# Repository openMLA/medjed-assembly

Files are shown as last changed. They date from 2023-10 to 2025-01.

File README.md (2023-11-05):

# Medjed Assembly

This repository contains the CAD files and assembly of the [MEDJED Maskless lithography system](https://github.com/openMLA/Medjed). CAD files are generated with FreeCAD.

Note that the [Wiki](https://github.com/openMLA/Medjed/wiki) and [Discussions](https://github.com/openMLA/Medjed/discussions) for the project are located in the main Medjed repository.

### Organisation

This repository should generally be obtained as a submodule of the main Medjed repository. That other repository will also have code and PCB designs for the project. 

The binary files are managed through [git-annex](https://git-annex.branchable.com/). When you first clone this repository these files will not have been downloaded, so you will see the history of the files, but not be able to open them.

To download these files, simply run (in git bash, or some terminal with git support)

``` shell
git-annex get .
```

Which should download all the files. If you only want a subset of the files, you can also run e.g. ` git annex get /optics/*.FCStd`. The files are stored on a [google cloud storage special remote](https://gist.github.com/NemoAndrea/86f93e55a579ad4e2c7e8fea4603c1c2).

### Freecad Configuration

The project uses two FreeCAD plugins, and it is recommended you install these before working with the files. You can easily install these with the built-in plugin manager of FreeCAD.

1. [Assembly 4 workbench 🏗](https://github.com/Zolko-123/FreeCAD_Assembly4)
2. [Optics workbench 🔍](https://github.com/chbergmann/OpticsWorkbench)
3. [KicadStepUp ⚡](https://github.com/easyw/kicadStepUpMod)

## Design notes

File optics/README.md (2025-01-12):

# Medjed Optics



### A quick note on motivations

The optical design is not designed to reach the absolute lowest cost possible, but rather prioritises the long-term availability of the components and ease of part sourcing. As such, many parts will be sourced from Thorlabs , and supplemented with 3D printed parts where possible. When components are chosen, they will still generally be on the lower-end of parts, as the Medjed is not a high resolution optical system (compared to what one may typically make with Thorlabs parts.)

For more detailed justifications for part choices and focal length, consult the [wiki page](../../Medjed.wiki/optics.md)



### A note on organisation

There are 3 different big assemblies in the origin. This is a bit confusing, but this was the only way to get around the "1 assembly per file" constraint of the `Assembly4` workbench. 

1. `assembly-optical` is the base assembly, which contains the base UV unit of the Photon Ultra.
2. `assembly-optical-stock` is the optical assembly, as used in the photon ultra (i.e. base assembly + lens)
3. `assembly-optical-medjed` is the main optics for the Medjed system.  **🔎 This is the main file to explore.**

## ☀ Ray Tracing with the Optics workbench

For the 60mm doublet I have used a fixed refractive index evaluated at 630nm. This is because the optics workbench does not support Cauchy coefficients, which are [the ones listed for the glass variants used in the lens](https://refractiveindex.info/?shelf=glass&book=HOYA-FD&page=E-FD10).

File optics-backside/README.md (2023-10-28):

### External models

The model for the Raspberry Pi Camera V2.1 was created by thingiverse user `soswow` and is available at https://www.thingiverse.com/thing:2376448/files.     The model was downloaded as an `.igs` file on 2023-06-11 and modified for purposes of the project.

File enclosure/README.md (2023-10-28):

## Medjed Enclosure

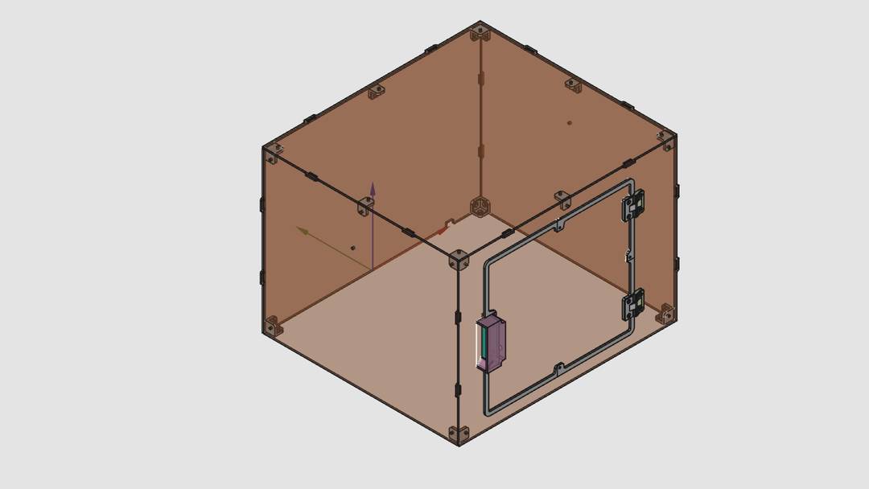
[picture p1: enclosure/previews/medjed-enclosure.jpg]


The FreeCAD file in this directory can be used to export `.dxf` files that define cut lines for acrylic panels.  In addition, there are printed parts that can be printed on a standard filament 3D printer. PLA is probably adequate, but if you plan on treating it particularly aggressively you may want to print the structural pieces out of PETG.

Use the **legacy** exporter for dxf, as the new one has some issue at time of writing (2023).

There are 5 panels total

* Front panel (this one is kept as a solid piece, to lower costs; some separation needed when you receive it)
* Back panel
* Side panel 1
* Side panel 2 (identical to panel 1)
* Top panel



The design features print-in-place hinges, which seem to print fine out of PLA, long term durability unknown. Print settings: Prusa Mini+. Polyterra PLA, 0.4mm nozzle, 0.2mm layer height.



###  Parts list

1. Acrylic panels (3mm thick; for thicker panels you need to adjust the designs a bit)
2. 3D printed parts (PLA seems to work OK, PETG preferred)
4. [Omron micro switch: D2F-01F-D](https://nl.rs-online.com/web/p/micro-switches/6867688)
5. M5 nut (with plastic collar would be preferred) [4X]
6. M4 bolts (10mm shaft length) and nuts (with plastic collar would be preferred) [35X]
7. M2 bolts and nuts for micro switch attachment [2X]

### Material choice

I suggest you have the enclosure cut out of orange acrylic. Ideally, choose an acrylic material of which you know the absorption at the relevant wavelengths (centered at 405nm, but consider 390-420). It would be good to have the enclosure made out of material with high absorption in this range (99.9%+). Since the focus of the objective (and hence the UV) is always far away from the user (provided they are not inside the enclosure) very high OD is not needed I suspect (please check safety considerations by yourself).

Something like 

* Plexiglas `ORANGE 2C04`
* Green Cast `orange`

*Note that neither of the above have published transmission spectra (that I could find), and may still transmit a significant amount of UV light.*

> **Note**
>
> There is a small test object in the main freecad file that you can order before ordering the main pieces. That tolerance piece can help you tune the tolerances of your cut acrylic supplier.

### A note on DXF export

The FreeCAD `.dxf` export produces files that may not be interpreted correctly by all manufacturers. A solution it to take legacy-dxf export from FreeCAD and open and re-export it via Fusion360. 

If you don't need to modify the panels yourself you can also use the provided [`.dxf` files](./dxf)

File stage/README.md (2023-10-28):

# XY stage

The XY stage has the following limits:

---

With Base 4-inch stage

X: 158mm (Z-axis prevents movement)

Y: 168mm 

---

With no stage (just the snapmaker carriage)

X: 168mm 

Y: 168mm 

## Sample chuck

The sample chuck PCB would ideally sit at such height that the UV sensor active area is exactly the sample height. For a typical Si sample: 0.5mm. Doing so, however, would mean the PCB and components stick out above the chuck's surface level. I think this is not ideal as it limits the sample size but also increases risk of collision.

The three ICs on the frontside have the following max heights:

* ICM42605: 0.97mm
* OPT3002: 0.65mm
* SHT45 (with PTFE filter): 0.79

Accounting for solder height and maybe poor seating I think recessing the PCB surface 1.5mm below the chuck should be adequate.

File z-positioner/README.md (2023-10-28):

## Fine Z-axis

The Medjed system needs to be able to focus the objective with a precision at least as good as the lateral resolution (5um target). The coarse Z-motors will not even get close to this. 

Thus, a separate fine focus mechanism is needed. 

**🏗 This this still in the prototype phase, please check out the GitHub discussions to see latest in development and experiments regarding this component.**

### Z positioner based on linear rail

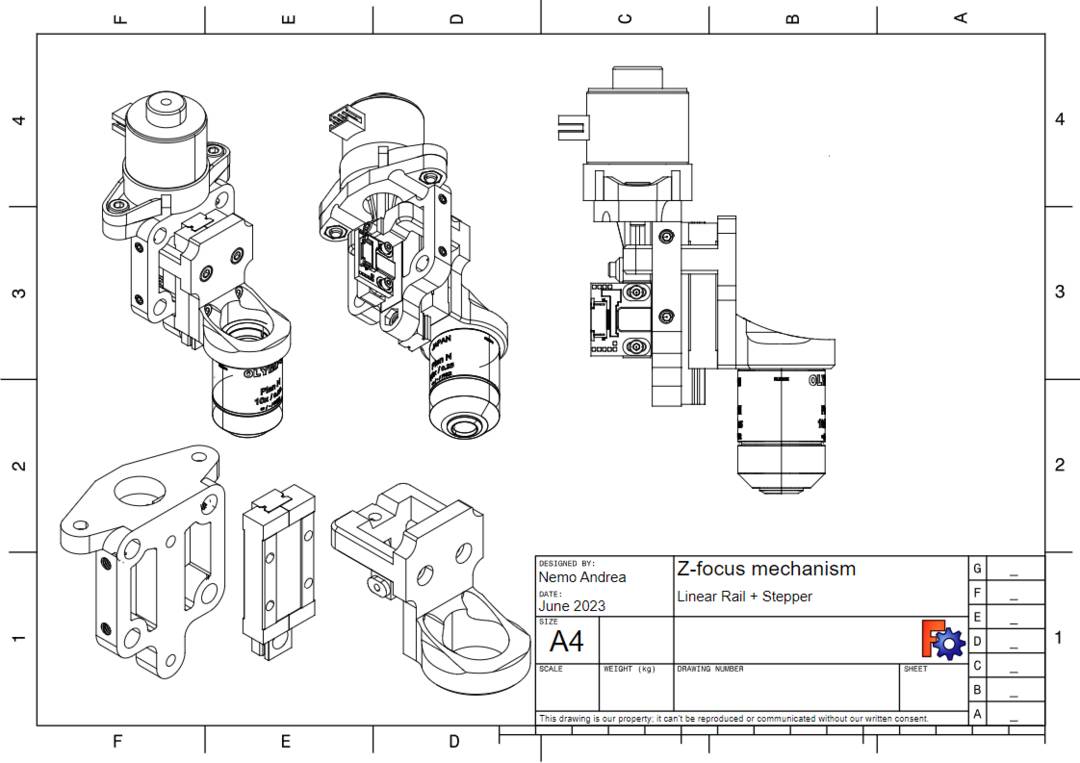
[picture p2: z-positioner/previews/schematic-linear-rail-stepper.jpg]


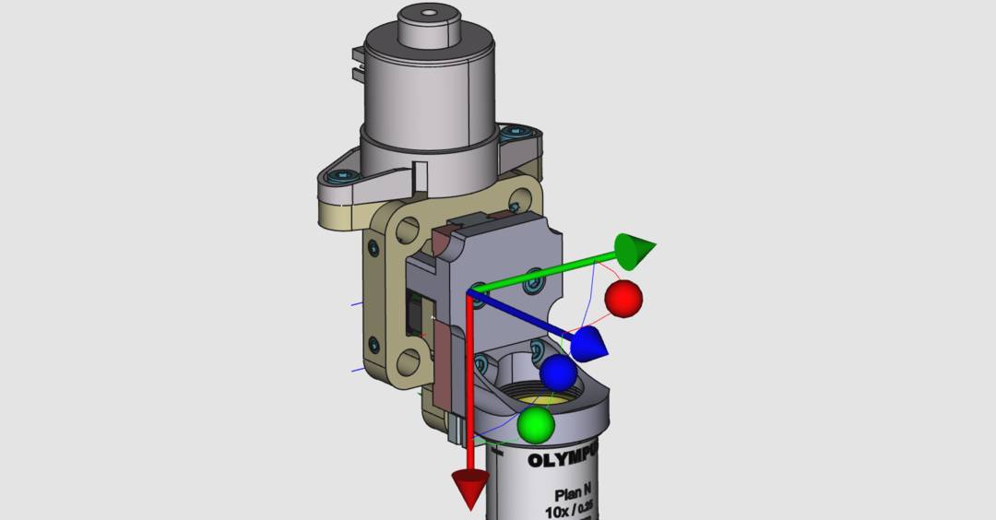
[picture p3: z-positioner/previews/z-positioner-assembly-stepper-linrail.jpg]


[Open in FreeCAD](z-positioner-assembly-stepper-linrail.FCStd)

Besides the linear rail, and encoder, you will need the following bits:

* 2x M4 (ISO 4762) bolts for stepper mount. 8 or 10 mm length.
* 2x M4 hex nuts (ISO 4032)
* 4x M3 4mm (ISO 4762) to mount objective bracket to rail
* 2x M3.5 8mm (ISO 4762) to mount rail to cage bracket
* 2x M3.5 hex nuts (ISO 4032)
* 4x M4 grub screw (ISO 4026) to secure the part against the cage rods
* 2x M2 10mm (ISO 4762) for encoder mounting
* 2x M2 hex nuts (ISO 4032)

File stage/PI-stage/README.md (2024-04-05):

# Physik Instrumente Stage

For development purposes, a PI M-525.2MO stage will be used. It uses small crossed roller bearings and stepper motors (M-229.25S; 10um backlash, 2um repeatability). The Steppers and encoders can be read out via python with the `pipython` python package.

A basic stage is built up around this system.

In the final product a custom replacement for the stage will be required, as it is neither fast enough, nor cheap enough to really serve as a good fit for the Medjed project.

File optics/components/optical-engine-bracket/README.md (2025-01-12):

# Optical Engine Bracket

This part connects the eViewTek optical engine to the rest of the build.

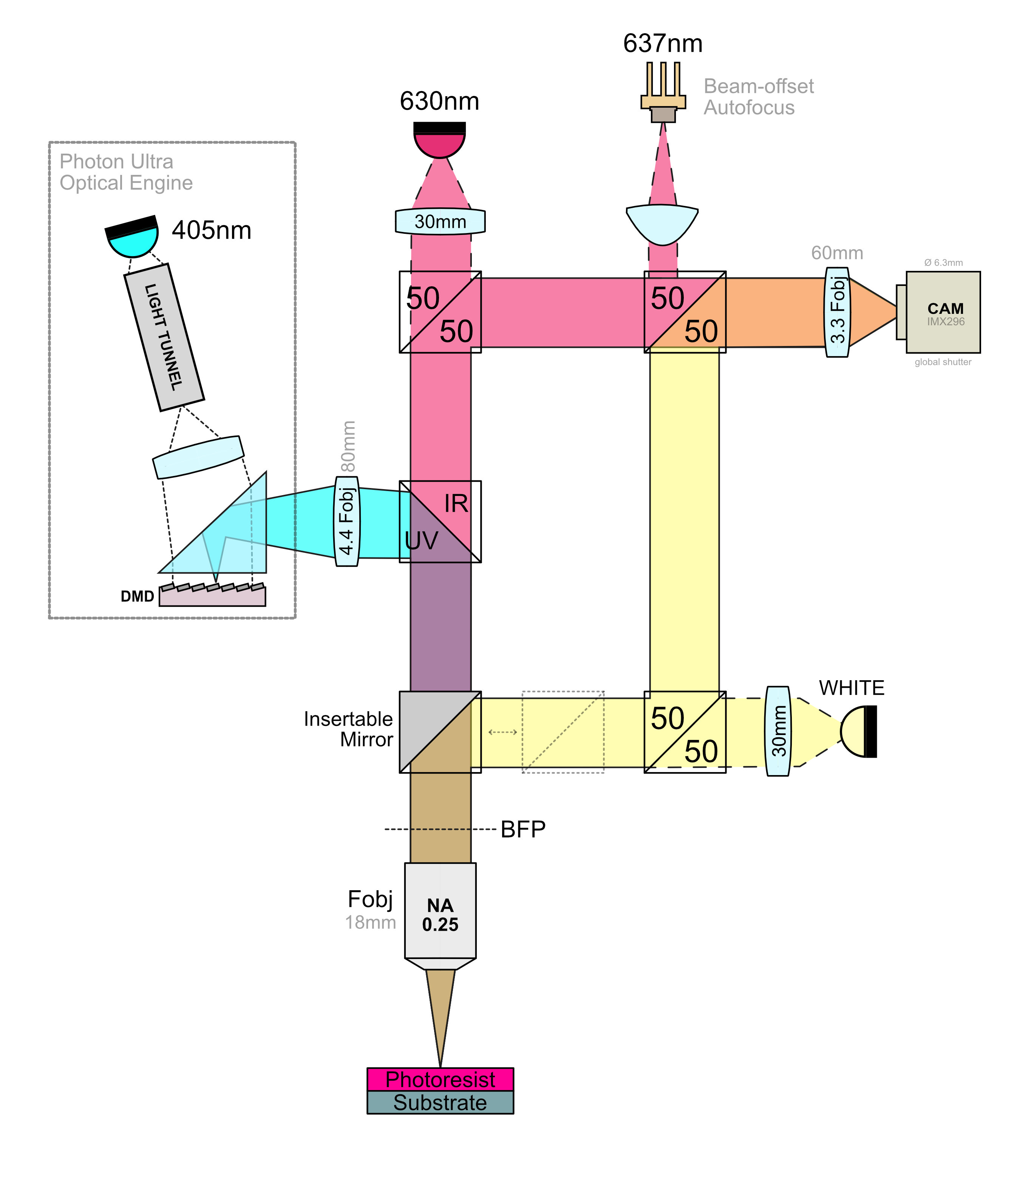
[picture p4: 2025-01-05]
media/optical_diagram.jpg

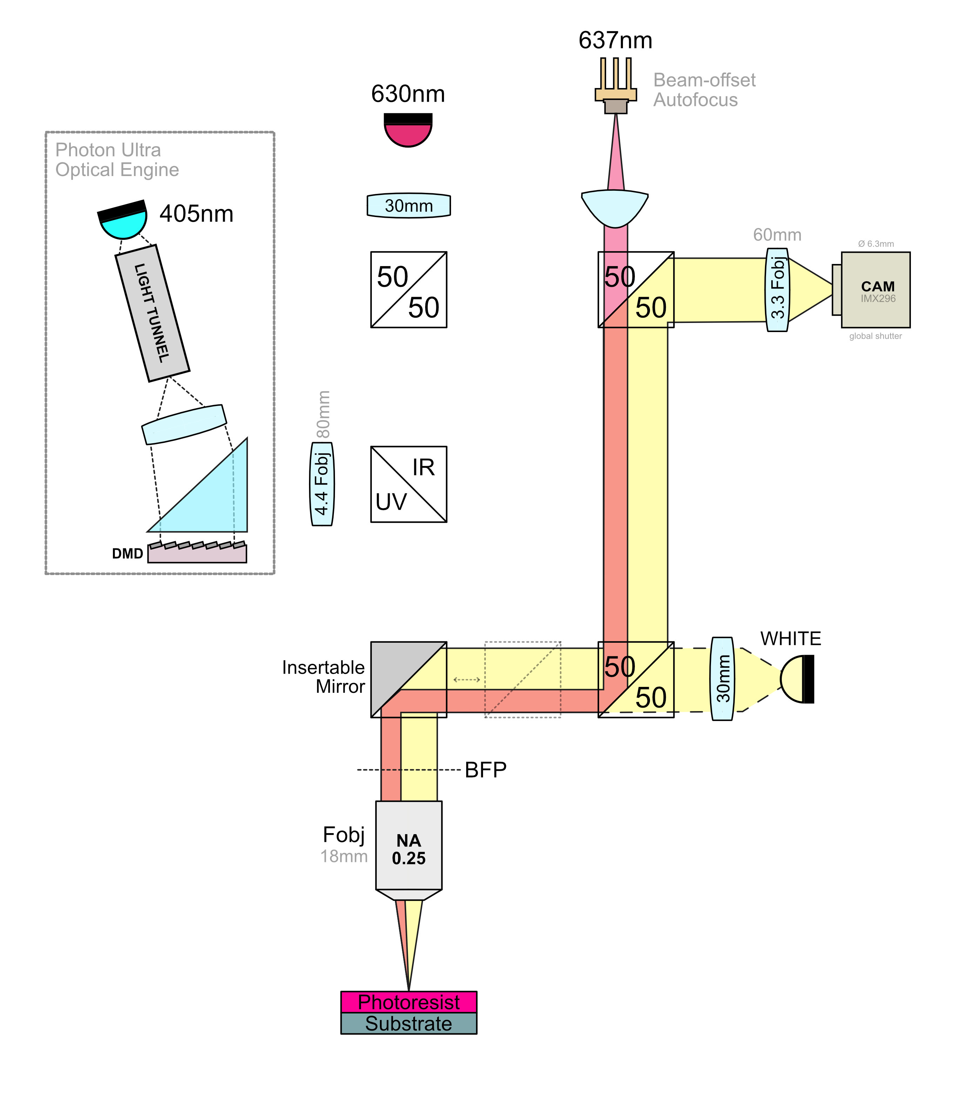
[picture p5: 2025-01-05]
media/optical_diagram-whitelight.jpg

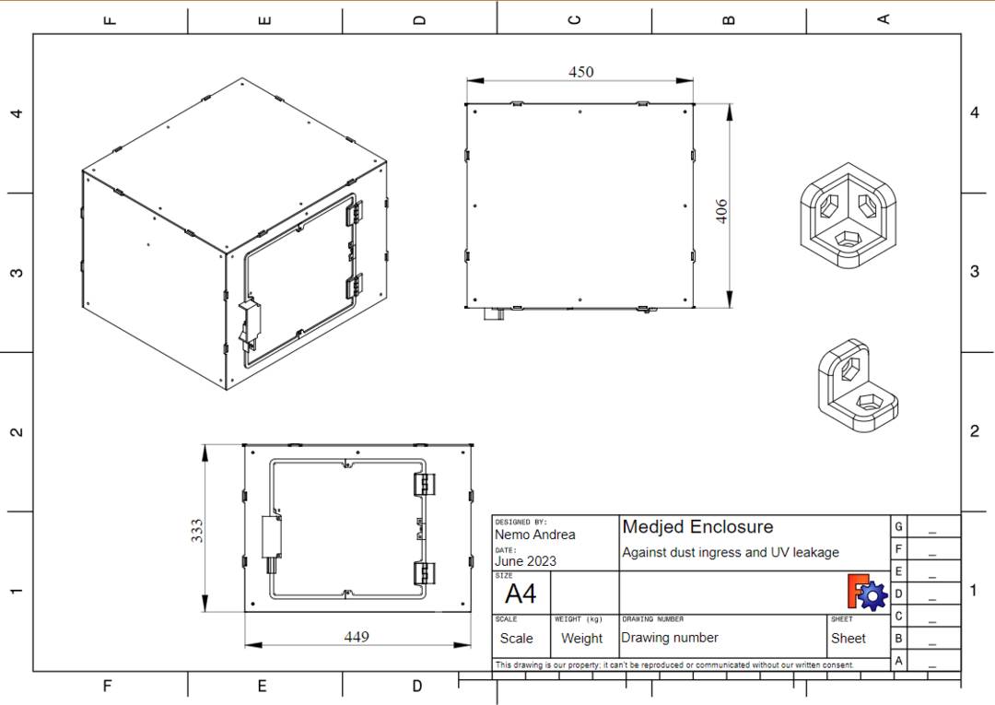
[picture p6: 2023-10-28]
enclosure/previews/schematic.jpg

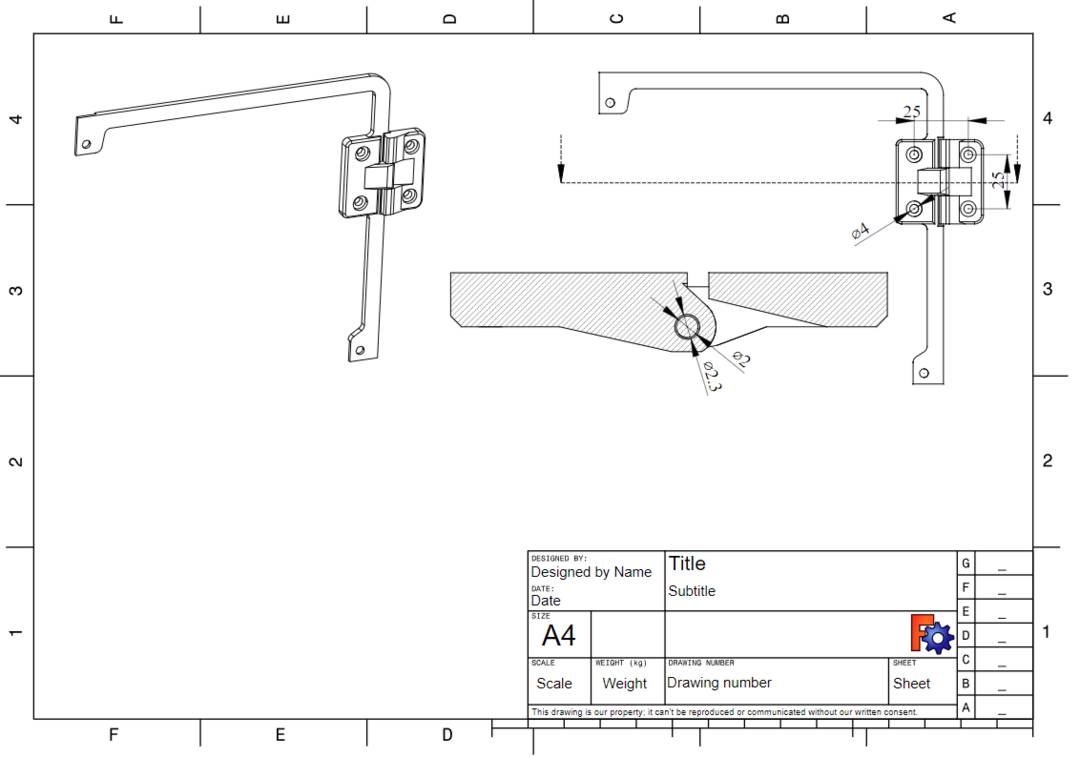
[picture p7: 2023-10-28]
enclosure/previews/schematic-hinge.jpg

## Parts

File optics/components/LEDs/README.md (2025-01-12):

## LED PCBs

These PCBs use a Cree XP-G3 LED. They were purchased from [led-tech.de](https://www.led-tech.de/) with parts indicators:
* `CREE-XP-G3-Photo-Red-on-Star`
* `CREE-XP-G3-R3-CRI-90-on-Star`

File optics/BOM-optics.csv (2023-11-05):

Name | Manufacturer | Manufacturer Number | Supplier | Supplier Number | Quantity | Price Total | Optional | Comments
Photon Ultra | Anycubic | 4.27E+13 | 3dprima | 27344 | 1 | 330 |  | To salvage DMD unit from
Optical cage rods 6mm |  |  | Thorlabs | ER12 | 4 | 80
30mm cage plate Metric |  |  | Thorlabs | CP33/M | 2 | 42
Olympus 10X PlanC N | Olympus/Evident |  | Astroshop.be | 49913 | 1 | 196 |  | Alternatively you can get the Japan-made version for ~400; optical design should be identical
Raspberry Pi global shutter camera | Raspberry Pi |  | Kiwi Electronics | KW-3146 | 1 | 60 |  | C/CS mount is preferred
Raspberry Pi high quality camera | Raspberry Pi |  | Kiwi Electronics | KW-2906 | 1 | 60 |  | C/CS mount is preferred
Enconomy Beamsplitter 1" |  |  | Thorlabs | EBS1 | 1 | 41
Enconomy Beamsplitter 1" |  |  | Thorlabs | EBS1 | 1 | 41 | WLM | For white light module
Cold mirror 1" |  |  | Thorlabs | FM04 | 1 | 51.9
Tube lens DMD 1" 80mm |  |  | Thorlabs | AC254-080-A | 1 | 96.07
Tube lens WLM 1" 75mm |  |  | Thorlabs | AC254-075-A | 1 | 96.07 | WLM | For white light module
Tube lens MARKER/AUTOFOCUS 1" 60mm |  |  | Thorlabs | AC254-060-A | 1 | 96.07
Biconvex lens MARKER/AUTOFOCUS illumination 1" |  |  | Thorlabs | LB1757-A | 1 | 45.48 |  | Placeholder
Biconvex lens WLM illumination 1" |  |  | Thorlabs | LB1757-A | 1 | 45.48 | WLM | Placeholder. For white light module
Silver mirror 1" |  |  | Thorlabs | ME1-P01 | 1 | 36.95
Silver mirror WLM 1" |  |  | Thorlabs | ME1-P01 | 1 | 36.95 | WLM | For white light module
LED illumination board MARKER/AUTOFOCUS | Adafruit | 2226 | Kiwi Electronics | ADA-2226 | 1 | 7.5 |  | Placeholder
LED illumination board WLM | Adafruit | 2226 | Kiwi Electronics | ADA-2226 | 1 | 7.5 | WLM | Placeholder. For white light module
M4 Setscrews |  |  | Thorlabs | SS4MS5 | 1 | 6.35 |  | pack of 50 setscrews

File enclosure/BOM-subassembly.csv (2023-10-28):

Name | Manufacturer | Manufacturer Number | Supplier | Supplier Number | Quantity | Price Total | Optional | Comments
Omron Micro Switch | Omron | D2F-01F-D | Mouser | 653-D2F-01F-D | 1 | 0.98 |  | For interlock. Also available at RS at MOQ 5
Polyimide hinges | Pinet | 54-A-3031 | RS components | 407-6950 | 2 | 17
M4 Inbus bolt 10mm |  |  | Generic | XX001 | 25 | 2.5
M4 Inbus nut |  |  | Generic | XX002 | 25 | 1.25
Emergency Off button | IDEC | YW1B-V4E02R | RS components | 168-2546 | 1 | 18.48 | EXTRA

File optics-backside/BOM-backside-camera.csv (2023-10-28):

Name | Manufacturer | Manufacturer Number | Supplier | Supplier Number | Quantity | Price Total | Optional | Comments
Pi Camera V2.1 noIR | Raspberry Pi | - | Kiwi Electronics | KW-1703 | 1 | 28.95 | BSA
Motic 10X Objective RedLine200 | Motic | 12220181 | astroshop.be | 567HJ | 1 | 39 | BSA | Finite conjugate
LED illumination |  |  | Adafruit | 1643 | 1 | 9 | BSA | Very preliminary pick; may need a simple custom board

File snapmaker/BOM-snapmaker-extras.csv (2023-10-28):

Name | Manufacturer | Manufacturer Number | Supplier | Supplier Number | Quantity | Price Total | Optional | Comments
Snapmaker power supply | Snapmaker |  | 3D Jake | SM-B.1.B.A.0002-01 | 1 | 69 |  | Price seems to fluctuate; see if you can pick it up for <90 otherwise pick up the internal supply directly (see other entry in BOM)
Barebones power supply | Meanwell | RSP-320-24 24V | Mouser | 709-RSP320-24 | 1 | 76.77 | ALT | Replacement for nicely enclosed snapmaker power supply; less powerful unit would probably work just as well; space for future optimisation
Snapmaker axis splitter (converter) | Snapmaker |  | 3D Jake | SM-B.1.H.A.0001-01 | 2 | 25.98 |  | Splits step/dir and can bus between two axes (for coarse Z axis)
M4 Inbus bolt 10mm |  |  | Generic | XX001 | 28 | 7 |  | for brackets

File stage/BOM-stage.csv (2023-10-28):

Name | Manufacturer | Manufacturer Number | Supplier | Supplier Number | Quantity | Price Total | Optional | Comments
Snapmaker linear axis 2.0 A150 for X and Y | Snapmaker |  | 123-3D | DAR00374 | 2 | 240 |  | For now only the 250mm version is available; design is built around the 168mm variant
RLS encoder RLC2IC |  |  | RLS | RLC2ICA13BB13A00 | 2 | 163.9
RLS magnetic tape 210mm with ref mark |  |  | RLS | MS05DM210AM027 | 2 | 70.76
M4 Inbus bolt 10mm |  |  | Generic | XX001 | 12 | 3
M5 heat inserts | Ruthex |  | 3DJAKE | RUT-GE-M5x95-001 | 1 | 10 |  | For vacuum fitting; pack of 50; ask a friend if they have something like it to save some money
M4 heat inserts | Ruthex |  | 3DJAKE | RUT-GE-M4x81-001 | 4 | 9.5 |  | For attaching stage
M3 heat inserts |  |  | 3DJAKE | ISP-GWEM3 | 4 | 5.69 |  | 50 piece set; for vacuum region selection
Tetra APS150 pump | Tetra |  | Amazon.de |  | 1 | 17 |  | Stage vacuum pump when diaphragm is reversed; point for future improvement

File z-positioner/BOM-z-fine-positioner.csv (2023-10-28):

Name | Manufacturer | Manufacturer Number | Supplier | Supplier Number | Quantity | Price Total | Optional | Comments
Small non-captive stepper |  |  | Stepperonline | 28LN24L01-233 | 1 | 14.75
RLS encoder RLC2IC |  |  | RLS | RLC2ICA13BB13A00 | 1 | 81.95
RLS magnetic tape MS - 26mm |  |  | RLS | MS05DM026AM010 | 1 | 19 |  | 26mm with reference mark at 10mm. Back adhesive pre-applied.
SLS printed parts | fine z-axis |  |  | Vormz.nl |  | 1 | 24 |  | Price is approximation and might be higher depending on supplier of choice
MGN9H linear carriage and 50mm rail |  |  | Fermio.xyz | FLG-MGN-09H-50-SUS | 1 | 15 |  | Equivalents from other brands (better or cheaper) should work just fine

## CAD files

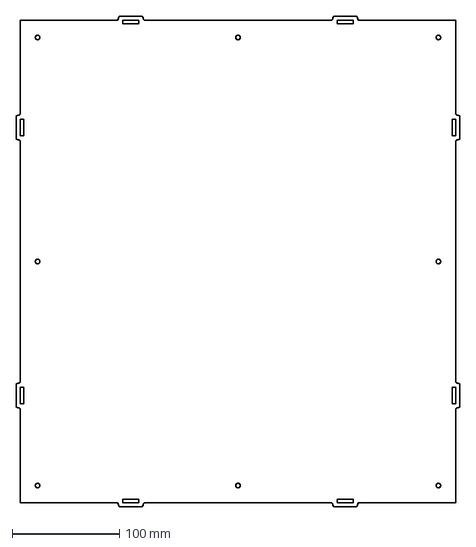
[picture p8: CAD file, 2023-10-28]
enclosure/dxf/toppanel.dxf
414.0 x 458.0 mm

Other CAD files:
medjed-assembly.FCStd
optics-backside/assembly-backside-optics.FCStd
optics/assembly-optical-medjed.FCStd
stage/assembly-stage.FCStd
z-axis-assembly/assembly-z-axis.FCStd
z-positioner/z-positioner-assembly-stepper-compact-flexure.FCStd
optics/assembly-optical.FCStd
stage/MainBoard-mount.FCStd
z-positioner/z-positioner-assembly-stepper-linrail.FCStd
z-positioner/z-positioner-assembly-stepper-flexure.FCStd
z-positioner/z-positioner-assembly.FCStd
enclosure/enclosure-door-sensor-omron-D2F.FCStd
enclosure/temp/drill_brackets.FCStd
jigs-and-tools/rpi-zero-cage-mount.FCStd
miscellaneous/heat-inserts.FCStd
optics/components/camera-mounting-brackets/raspberrypi_camera_mount.FCStd
optics/components/LEDs/cree-XP-G3-pcb.FCStd
enclosure/dxf/backpanel.dxf
enclosure/dxf/frontpanel.dxf
enclosure/dxf/sidepanel.dxf
enclosure/enclosure-acrylic.FCStd
enclosure/enclosure-hinges-pinot-40mm.FCStd
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

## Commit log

2023-10-28 Ïnitial annexed commit
    [45deg_cagebracket.FCStd, BOM-backside-camera.csv, BOM-optics.csv, BOM-snapmaker-extras.csv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]
2023-11-05 Move optics components to separate subfolder
    To organise the growing optics directory I will gradually move over components to their own subfolder if they are custom parts.
    [BOM-optics.csv, adafruit_LED_pcb_neopixel_jewel.FCStd, jewel-CP33-cage-plate-mount.FCStd, optical-engine-mount-bracket.FCStd]
2023-11-05 Move lens components into part design
    Moving some components into part design (rather than part) because the Optics Workbench doesn't support nesting.
    [assembly-optical-medjed.FCStd, thorlabs_AC254-060-A_lens_doublet_f60mm.FCStd, thorlabs_ACL25416U-A_aspheric_lens.FCStd, thorlabs_CP33_cageplate.FCStd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]
2023-11-13 Update lenses and finalise ray simulation
    [assembly-optical-medjed.FCStd, inline-1-inch-optic-holder.FCStd, thorlabs_AC254-060-A_lens_doublet_f60mm.FCStd, thorlabs_AC254-075-A_lens_doublet_f75mm.FCStd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]
2024-03-09 Reorganise optical engine files
    Clear up some legacy bloat by renaming and reducing the number of files.
    [eViewTek-optical-engine-and-lens.FCStd, eViewTek-optical-engine.FCStd, medjed-optics.FCStd, old-OE-assembly.FCStd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]
2024-03-09 Complete optical engine file reorganisation
    [eViewTek-optical-engine-and-lens.FCStd, old-OE-assembly.FCStd]
2024-03-09 Update with last horizontal optical assembly
    This is the final version of the horizontal optical assembly, before moving to a more gravity-friendly vertical arrangement.
    [assembly-optical-medjed.FCStd]
2024-03-11 early vertical optical assembly
    [assembly-optical-medjed.FCStd]
2024-04-05 Add design files for PI stage
    Add design files for the (temporary) PI M-525.2MO stage that will be used during the testing phase. Not really meant for reproduction, but the files may be interesting for someone rolling their own b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
    [pi-stage-M525.2M0.FCStd]
2024-10-14 Add new short stroke linear axis
    Created with new Ondsel ES FreeCAD based platform
    [dold_mechatronik_linear_guide_ST07.FCStd]
2024-10-14 Update optical diagram
    New diagram more closely represents the current arrangement of elements. Minor edits to optics readme.
2024-10-14 Minor and major revisions to many components
    Commiting all together to ensure the major assemblies are functional when cloned from scratch.
    [Objective_Olympus_PlanN_10X.FCStd, RMS_cage_plate_90deg.FCStd, adafruit_LED_pcb_neopixel_jewel.FCStd, assembly-optical-medjed.FCStd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]
2025-01-05 Aggregate project changes prior to FreeCAD 1.0 migration
    [Objective_Olympus_PlanN_10X.FCStd, adafruit_LED_pcb_neopixel_jewel.FCStd, assembly-optical-medjed.FCStd, backpanel_fusion360.dxf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]
2025-01-10 Remove raytracing elements and clean up main optical assembly
    Pushing back the move to 1.0 assembly system due to instability of that system in current stable build. For now removed the raytracing from the main assembly document to keep it more lightweight and 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
    [assembly-optical-medjed.FCStd]
2025-01-11 Rework baseplate and stay with assembly4
    Did a lot of work on making the assembly revolve around stable sketches of the baseplate object. I think that is the way to go. Now have responsive alignment edges for various optical components. Sti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
    [camera_RPi_global.FCStd, dold_mechatronik_linear_guide_ST07.FCStd, raspberrypi_camera_case.FCStd, raspberrypi_camera_mount.FCStd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]
2025-01-12 Complete alignment brackets and tuned lens distances
    Finalised the alignment brackets and interactive alignment options. Tuned lens distances for laser, LEDs, and cameras. Changed the bulk shape of the baseplate a bit and added a raspberry pi in a temp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
    [assembly-optical-medjed.FCStd, camera_RPi_global.FCStd, dold_mechatronik_linear_guide_ST07.FCStd, eViewTek-optical-engine.FCStd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]
2025-01-12 Move to new LEDs
    Move to new LED boards using CREE leds. These are not neopixels, so brightness and CRI should be better.
    [adafruit_LED_pcb_neopixel_jewel.FCStd, assembly-optical-medjed.FCStd, cree-XP-G3-pcb.FCStd, jewel-CP33-cage-plate-mount.FCStd]
